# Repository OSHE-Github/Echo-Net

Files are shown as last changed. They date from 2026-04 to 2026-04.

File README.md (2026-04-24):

# Echo-Net

This project aims to assist bat research by creating a small lightweight external RFID tracking device. This device would allow researchers to easily tag bats with external tags, reducing the invasiveness of the process and allowing them to obtain data on the movement of bats. 

While these devices are being developed with the intention of bats in mind their applications can stretch beyond that of bats. This project sets a platform for using small RFID tags to track not just animals but anything that can be tagged, allowing for branching in fields such as inventory management or item tracking.

<div align="center">
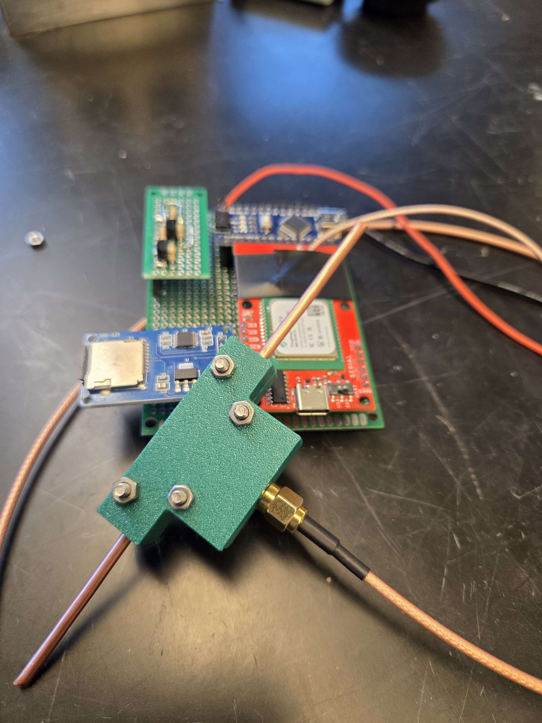
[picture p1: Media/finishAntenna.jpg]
Final Assembled Reader


Figure 1: Final Reader Prototype
</div>

# Problem Statement
In the UP bats are being killed due to an invasive fungus called the white noise fungus. This is causing a sharp decline in the bat population. A group of researchers at the Michigan Technological University CFRES Department are working to research these bats and attempt to counteract the effects of this fungus. One of their goals is to track the movement of the bats during the winter months, evaluating how they travel between hibernaculums. 

Their current strategy for tracking the bats is color tags which are attached to the wing of the bat and then manually counted through the winter to get a rough estimate of their movement patterns. The goal of this project is to design a system that utilizes small RFID tags to track the bats remotely through a system at the entrance of the cave to determine when and where the bats are moving. In addition a handheld device will also be designed for the cave to be swabbed for the current bat that are present.

# Methodology
## Overview 

To start the design a general block diagram of the system was laid out as seen in Figure 2. This system has three main sections, one of which was manually focused on this semester in the data. The power system was also evaluated, and the interrupt system was left for future semesters.

<div align="center">
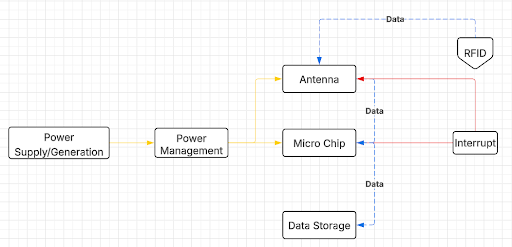
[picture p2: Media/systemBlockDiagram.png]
System Block Diagram for Reader


Figure 2: System Block Diagram for Reader
</div>

## Power

Solar energy was evaluated early in the design process but rejected due to the persistent snow cover that would obscure panels for weeks or months, and the maintenance challenges, as clearing snow is not feasible for this remote operation.

Given these constraints, wind energy was the only viable renewable power source capable of providing continuous, unattended operation throughout the winter season.

The turbine was developed for deployment near cave environments where bat activity is dense and unpredictable. Because of this, the mechanical subsystem had to meet strict biological safety requirements. The project guidelines emphasized that no component of the power-generation system could pose a serious risk of injury to the bats.

Traditional horizontal‑axis turbines with exposed, high‑speed blades were immediately ruled out due to their high tip‑speed ratios that could harm the bats.

To satisfy the safety requirement while still enabling continuous power generation, we selected a helical‑bladed VAWT. This geometry offers several advantages in a cave‑adjacent or wildlife‑dense environment. First, there is no high‑speed blade tips because the rotational velocity is distributed more evenly along the height of the rotor. Also, there is a smooth, continuous surfaces that reduce the likelihood of injury upon incidental contact. Additionally, it has omnidirectional operation, eliminating the need for yaw mechanisms or exposed linkages. Another benefit is its lower startup torque compared to some HAWT designs, which is beneficial in low‑wind cave entrances. The helical profile also ensures more uniform torque production over the rotation cycle, reducing vibration and mechanical stress on the generator shaft.

The entire embedded system requires a small but continuous power budget. Based on preliminary load analysis of the RFID reader, microcontroller, and data‑logging components, the turbine was designed to produce 0.5–1 W under typical winter wind conditions.

To meet the 0.5–1 W requirement, the a NEMA 23 stepper motor was chosen for the design, which demonstrated an approximate 12 V peak‑to‑peak open‑circuit voltage when spun manually at expected speeds.

## Data

The first part of the data system is the reader design, this encompasses the microcontroller and module board for reading the data from the tags as well as storing it on our SD card for later data analysis.
	
For our reader module we utilized the SparkFun Simultaneous RFID Reader M7E Hecto board, this board is able to read UHF RFID such as the ones that we are using. By utilizing this development board we were able to reduce the complexity of our RFID reader ensuring increasing the speed in which we could develop a working prototype and test the other components of our system.

For the microcontroller of our project we used an Arduino Nano. We chose to use this to do the simplest of implementing, there was discussion about using an Atmega328-PU for reduced power consumption but due to the ease of implementations of the Nano we ultimately went with it. In the future if power consumption becomes a problem the design may be changed to utilize something other than an Arduino to reduce power.

The rest of the reader design consisted of a logic level shifter and a SD card module. The level shifter allows for the 5V logic of the Arduino to be shifted to the 3.3V of the SparkFun M7E Hecto board. The SD card was used to store the data that was collected by the device for later data manipulation. A full schematic over our design can be seen in Figure 3.

<div align="center">
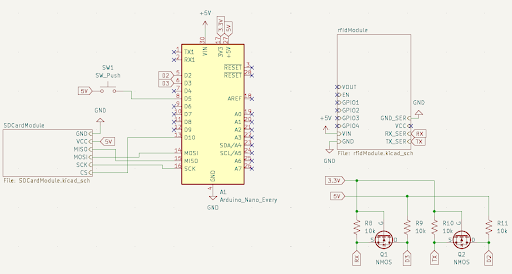
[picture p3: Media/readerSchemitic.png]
Reader Schemitic


Figure 3: Reader Schematic
</div>

The code for the reader is relatively simple. It leverages the example code from the SparkFun_UHF_RFID_Reader library constant reading example. With the addition of writing to the SD card through some simple helper functions the data collected on the SD card can be seen in Figure 4. There is also an option to enable a required trigger hold in order to start reading.

<div align="center">
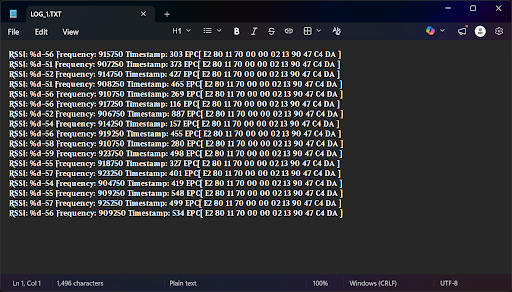
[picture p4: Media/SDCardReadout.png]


Figure 4: SD Card Data Collection Readout
</div>

The next stage in our data collected system is the antenna that is used to transmit to the tags. Three designs for an antenna were initially tested, a helical antenna, a clover leaf antenna, and a half dipole antenna. 

A ½ wave dipole antenna was decided on and constructed using copper pipe and a 3D-printed body. This resulted in an antenna that was durable, simple to construct, and lightweight/mobile. The dipole antenna was only decided on after both attempting to create other styles of antennas such as a helical and cloverleaf antenna, and after testing some 915MHz antennas we had lying around. 

The helical antenna was not selected due to its large size and directionality. It was difficult to get it aligned properly which resulted in missed reading. In addition its large size made it impractical for a hand held antenna. The cloverleaf's setbacks were in the form of its fragility and lower read range. With there being little structure to the cloverleaf, concerns around its ability to survive a winter in the cave resulted in the decision to favor the more robust half dipole design.

The initial design of this antenna was done in Matlab antenna designer, with a rendering of the half dipole antenna being seen in Figure 5. In addition the directivity of the antenna can be seen in Figure 5. This shows that the antenna can read the tags in any direction as it is circularly polarized.  Finally an S11 plot is in Figure 6, this plot as a dip at 915 MHz down to -15dB which shows that the antenna is most efficient at a frequency of 915 MHz which is desired.

<div align="center">
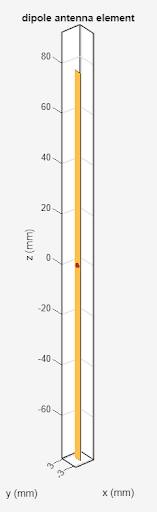
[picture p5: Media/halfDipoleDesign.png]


Figure 5: Half Dipole Antenna Design
</div>

<div align="center">
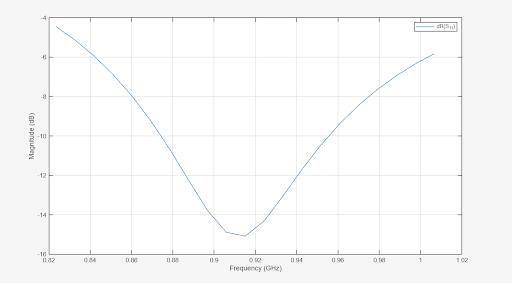
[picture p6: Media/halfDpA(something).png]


Figure 6: HalfDipole Antenna S11 Plot
</div>

The final part of our design was the selection of a tag which is attached to the bat. The tag was the Impinj Monza R6P, which can be read between the frequencies of 860 - 940 Mhz. It also has a small size of 2.6x2.6x0.8mm which help to reduce the weight that is attached to the bat.

<div align="center">
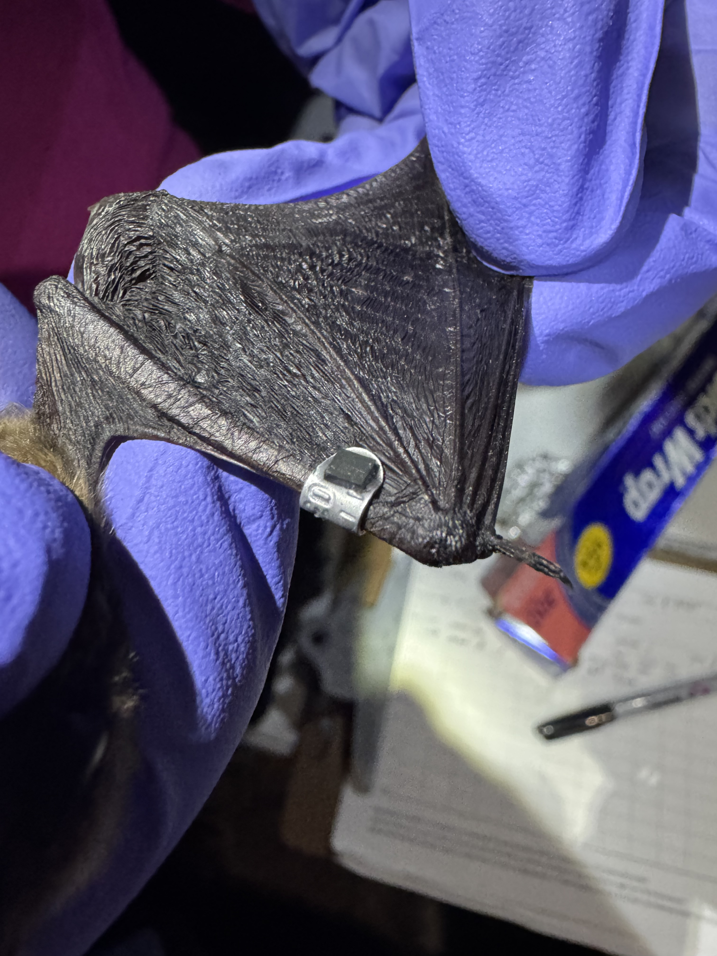
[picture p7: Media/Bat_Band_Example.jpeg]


Figure 7: Example of a Tag and Band Attached to a Bat
</div>

In addition to the tags internal antenna which is very small a circular antenna was attached to the tag as seen in Figure 8. This was done to increase the read range and directionality of the tag. By utilizing this the read range was able to be significantly increased along with making the tag easier to read in different orientations.

<div align="center">
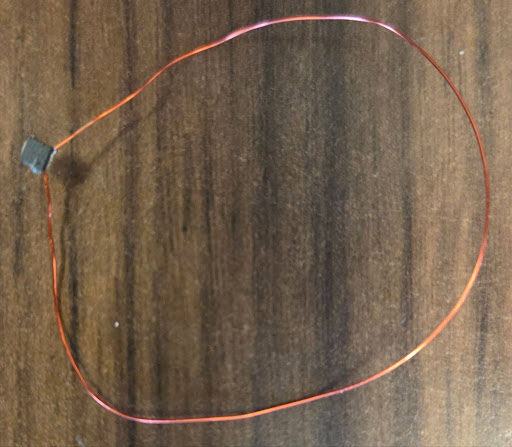
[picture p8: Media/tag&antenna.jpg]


Figure 8: Tag with Circular Antenna
</div>

# Results
## Power
The current motor in our turbine design can produce around 12V when spun in ideal condition as seen in Figure 9.  

<div align="center">
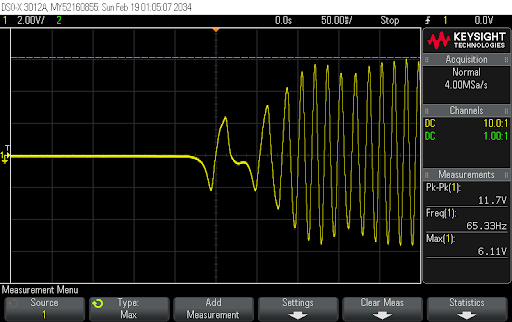
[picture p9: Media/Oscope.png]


Figure 9: Oscilloscope Readings 
</div>

To determine the amount of power that needed to be generated the power consumption of the read was measured at different dB output. The results of the this testing can be seen in Figure 10. The general operating range of this device is between  20-27 dB which means that on average  it will be consuming between 2-2.85 watts. This means that having the power completed provided my the turbine is impractical. To compensate for this battery options were evaluated.

<div align="center">
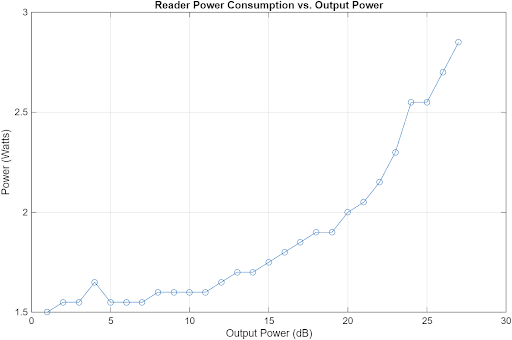
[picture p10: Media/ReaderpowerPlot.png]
Reader Schemitic


Figure 10: Read Power Consumption based on Output dB
</div>

The first battery option evaluated was a car battery that would be left at the stationary site to supplement the turbine. Assuming a car battery of 12.8V and 60 Ahr it can be determined that there 786 Whr. Assuming that there is 90% efficiency in the step down to operating voltage and that the battery should not be operated below 50%, as recommended for lead acid batterying the device could be powered for 3.83 days straight. 

Another option that was evaluated was a hand held power brick used for charging phones. An example that was found commercially available had an estimated 20,000 mAhr at 3.7V which equates to 74 Whr. Assuming the same 90% efficiency that was had with the car battery it was determined that the device could be powered for 17.8 hrs. This provides a viable hand held power solution in a light weight portable package

## Data

Using a Micro VNA the characteristics of out half dipole antenna were measured as seen in Figure 11, and summarized in Table x. This data is closely aligned with the that of the simulation with the desired S11 LOGMAG being around -15 dB and the impedance of the antenna being 50 Ω. 

<div align="center">
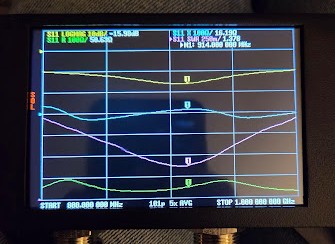
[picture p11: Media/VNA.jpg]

	
Figure 11. Nano VNA Data for Half Pole Antenna

Table 1. Data from Nano VNA for Half Pole Antenna 
| Parameter        | Setting | Value    |
|------------------|--------|----------|
| S11 LOGMAG       | 10 dB  | -15.98 dB |
| S11 R            | 100 Ω  | 50.63 Ω  |
| S11 X            | 100 Ω  | 16.19 Ω  |
| SWR              | 250 m  | 1.378    |
</div>

With this antenna design the read range was measured with 4 different configurations as seen in Figure 12. The first one was with the tag on the mental band. With this configuration no read range was able to occur. This was hypothesized to be due to the JB weld that was used to connect the tag to the band. This is further supported by the fact that when the tag is removed from the band but left in close proximity to the band the tag can be read. This leads to the belief that it is not the metal of the band that is hindering the read range. 

The next configuration that was tested was the tag with no band or additional antenna. The read range in this configuration was very limited, only around a few centimeters and was very orientation dependent. 
To compensate for the short read range a loop antenna was added to the tag to increase the range. This had an immediate effect with the read range jumping up to 1-1.5 meters and the tags being less orientation dependent while being read. In addition while not being consistent that the maximum range the tags were detected up to was 2.5m. 
<div align="center">
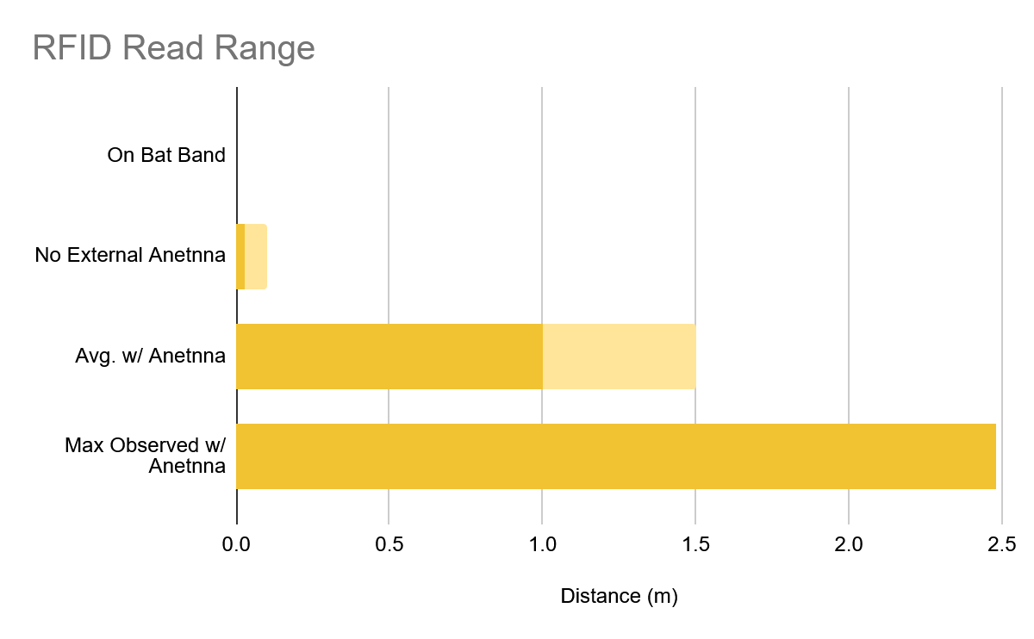
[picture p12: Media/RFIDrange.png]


Figure 12. Read Range of the Tags in Different Configurations
</div>

# Future Work
To advance this project forward custom flex PCBs will be designed such as the reference in Figure 13. This flex PCB will then be epoxied to the banners with the additional loop antenna confined with them. To determine the optimal antenna design multiple lengths, widths, and dielectrics will be tested. By creating a swab of these antenna designs it will be able to determine the ideal design for read range. 
<div align="center">
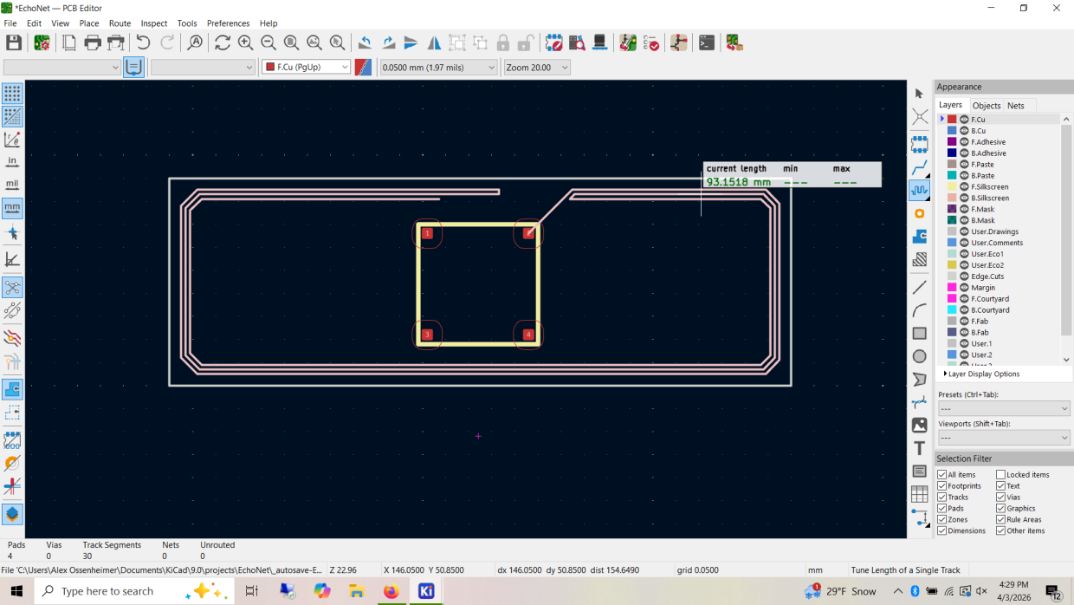
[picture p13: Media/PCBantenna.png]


Figure 13. Mock-Up of Possible PCB Antenna 
</div>

In addition to this a PCB will also be designed for the reader design. Currently it is only a prototype board which works great for testing and rapid prototyping but for future designs a PCB will be made to make it more robust and easier to assemble. 
Additional testing also needs to be completed for battery option testing. Two options were evaluated for viability but neither has yet been tested to confirm life span. In addition the trickle charge from the wind turbine should be added into the life span of the car battery option. In addition to this to decrease power consumption low power interpret monitoring can also be evaluated.

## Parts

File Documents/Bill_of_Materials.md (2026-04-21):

# Bill of Materials (BOM)

## Wind Turbine

| Part | Quantity | Price |
|------|----------|-------|
| [23HS45-4204S Nema 23 Motor](https://www.omc-stepperonline.com/nema-23-bipolar-3nm-425oz-in-8mm-diameter-4-2a-57x57x113mm-4-wires-stepper-motor-23hs45-4204s1) | 1 | $28.70 |
| [3' 6061 Solid Aluminum Rod 10mm Diameter](https://www.mcmaster.com/products/aluminum-rods/material~aluminum-2/material~6061-aluminum/) | 1 | $8.73 |
| [⅛" Aluminum TIG Welding Rods](https://www.airgas.com/product/Welding-Products/Filler-Metal/TIG-Rod-%28GTAW%29/TIG-Rod---Aluminum/p/RAD64001731) | 1 Tube | $19.81 |
| [10 mm Flanged Bearings](https://www.amazon.ca/uxcell-F6900ZZ-10x22x6mm-Shielded-Bearings/dp/B07Z3DQHLL) | 2 pcs (1 set) | $6.89 |
| [JB Weld KwikWeld](https://www.amazon.com/Epoxy-Adhesives-J-B-Weld/s?keywords=Epoxy+Adhesives&rh=n%3A256244011%2Cp_89%3AJ-B%2BWeld&c=ts&ts_id=256244011) | 1 pack | $5.93 |

## Dipole Antenna

| Part | Quantity | Price |
|------|----------|-------|
| [8 Gauge Wire](https://www.amazon.com/Tynulox-Refrigeration-Seamless-Jewellery-Industry/dp/B0BLNRQYZ4/ref=sr_1_4_sspa?s=industrial) | 2 x 73cm | $7.39 |
| [Male SMA Port](https://www.amazon.com/wlaniot-Connector-Coaxial-Bulkhead-Terminal/dp/B078H4F8R6/ref=sr_1_6) | 1 | $7.99 |
| [22 Gauge Wire](https://www.amazon.com/TUOFENG-Hookup-Wires-6-Different-Colored/dp/B07TX6BX47/ref=sr_1_8?s=industrial) | ~50cm | $15.89 |
| [PETG](https://www.prusa3d.com/product/prusament-petg-jungle-green-1kg-nfc/) | ~9.4g | $0.26 |

## Reader Module

| Part | Quantity | Price |
|------|----------|-------|
| [SparkFun Simultaneous RFID Reader M7E Hecto](https://www.sparkfun.com/sparkfun-simultaneous-rfid-reader-m7e-hecto.html) | 1 | $309.95 |
| [Arduino Nano](https://www.amazon.com/LUIRSAY-2Pcs-ATmega328P-Microcontroller-Compatible/dp/B0F1FQMNXM/ref=sr_1_1?hvqmt=e&mcid=8b35fce829b232af874780ddece88d5b) | 1 | $12.99 |
| [Prototyping Board](https://www.amazon.com/ELEGOO-Prototype-Soldering-Compatible-Arduino/dp/B072Z7Y19F/ref=sr_1_1_sspa) | 1 pack | $8.99 |
| [2.54mm Male/Female Headers](https://www.amazon.com/2-54mm-Breakaway-Female-Connector-Arduino/dp/B01MQ48T2V/ref=sr_1_6?s=industrial) | 1 pack | $7.99 |
| [10kΩ THM Resistor](https://www.digikey.com/en/products/detail/stackpole-electronics-inc/CF14JT10K0/1741265) | 4 | $0.10 |
| [VN2106N3-G BJT](https://www.digikey.com/en/products/detail/microchip-technology/VN2106N3-G/4902398) | 2 | $0.50 |
| [UFL to SMA Adapter](https://www.amazon.com/Ahoaepy-Coaxial-Pigtail-Extension-Antenna/dp/B0D29JTYPK/ref=sr_1_2_sspa?hvlocint=4089&hvqmt=e&mcid=b62bc0d9b4873ecfa4f331e8886e656e) | 1 | $7.19 |
| [SMA Male to Male Jumper](https://www.amazon.com/coaxial-Antenna-Extender-Adapter-Jumper/dp/B092Z88R2T/ref=pd_sbs_d_sccl_2_11/138-8639619-0532315) | 1 | $8.99 |
| [SD Card Module](https://www.amazon.com/Integrated-Circuit-Interface-Raspberry-Breakout/dp/B08C4WY2WR/ref=sr_1_5?hvqmt=e&mcid=e3acc2ea9a2638039ac6f78958a5b55b&s=electronics) | 1 | $5.99 |

## Total Cost: $504.07

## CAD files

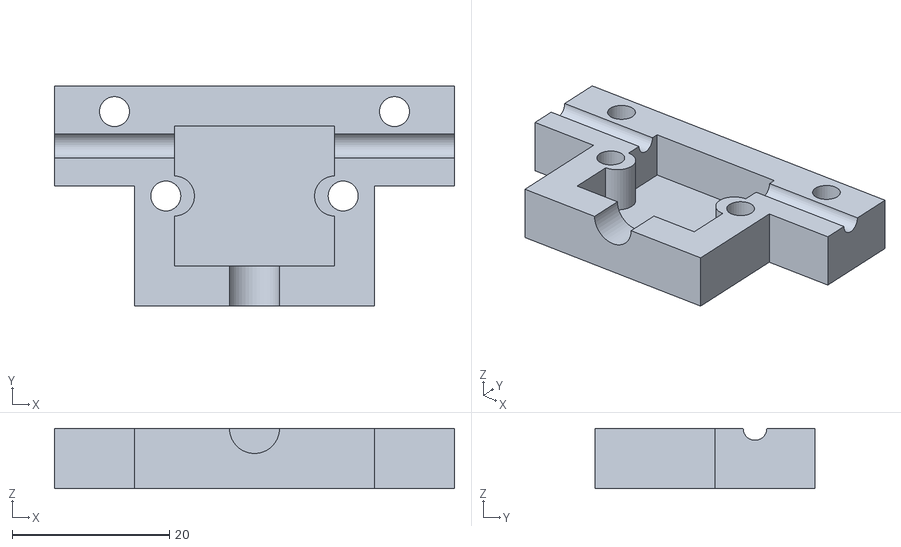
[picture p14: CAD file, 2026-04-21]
CAD/Antenna/Dipole_Antenna_Shell.stl
50.8 x 27.9 x 7.62

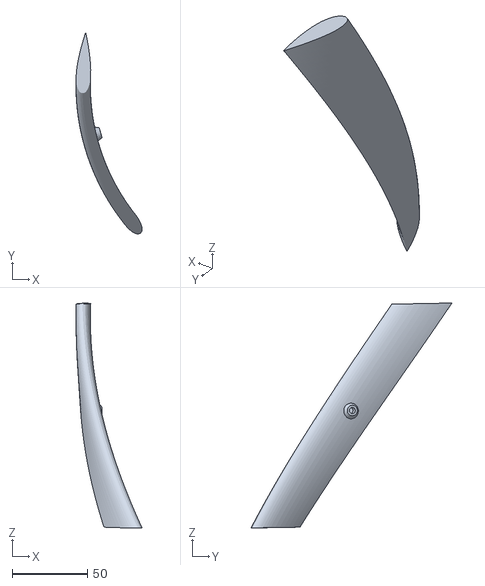
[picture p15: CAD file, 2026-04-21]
CAD/Turbine/VAWT_Fin_Top.stl
43.8 x 133.3 x 149.2

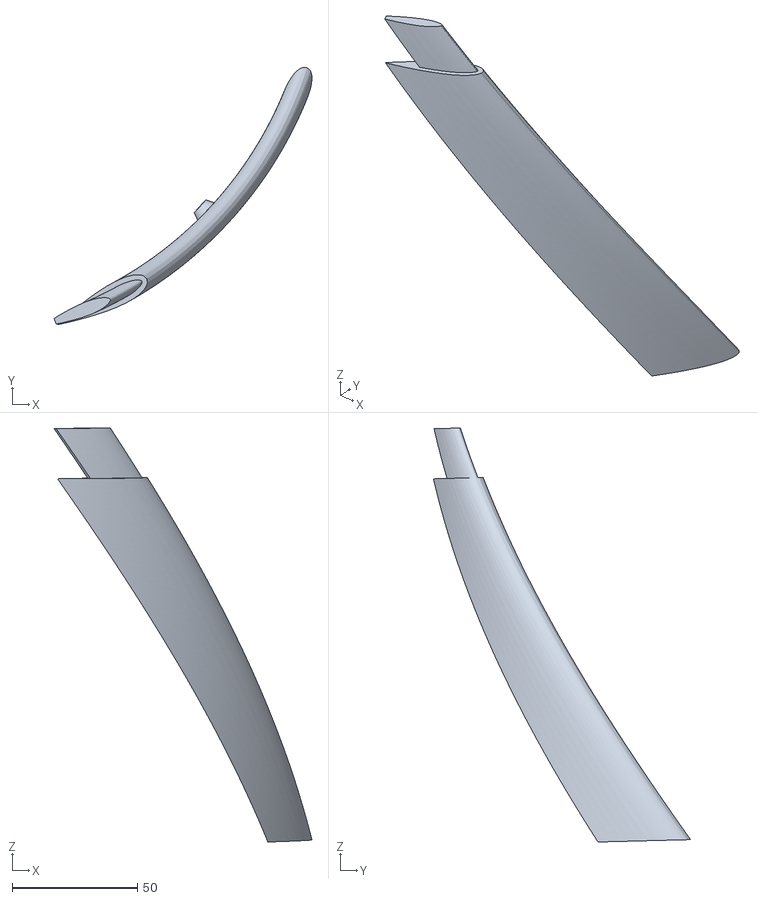
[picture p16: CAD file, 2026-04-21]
CAD/Turbine/VAWT_Fin_Bottom.stl
103.0 x 102.7 x 165.3

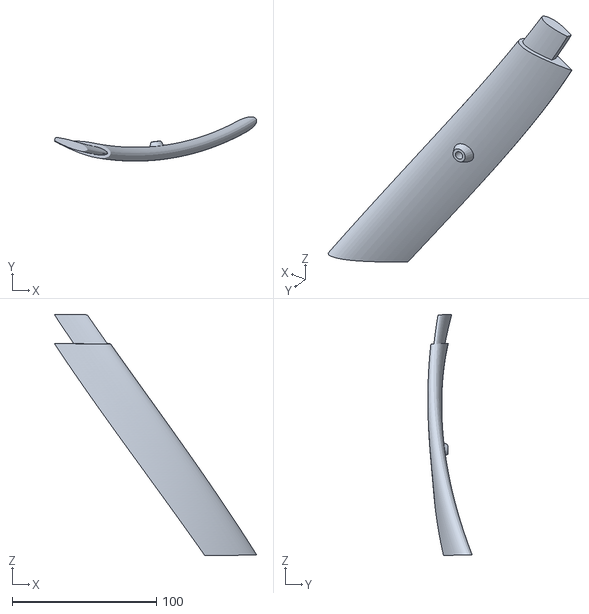
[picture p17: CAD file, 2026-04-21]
CAD/Turbine/VAWT_Fin_Middle.stl
140.1 x 30.7 x 166.9

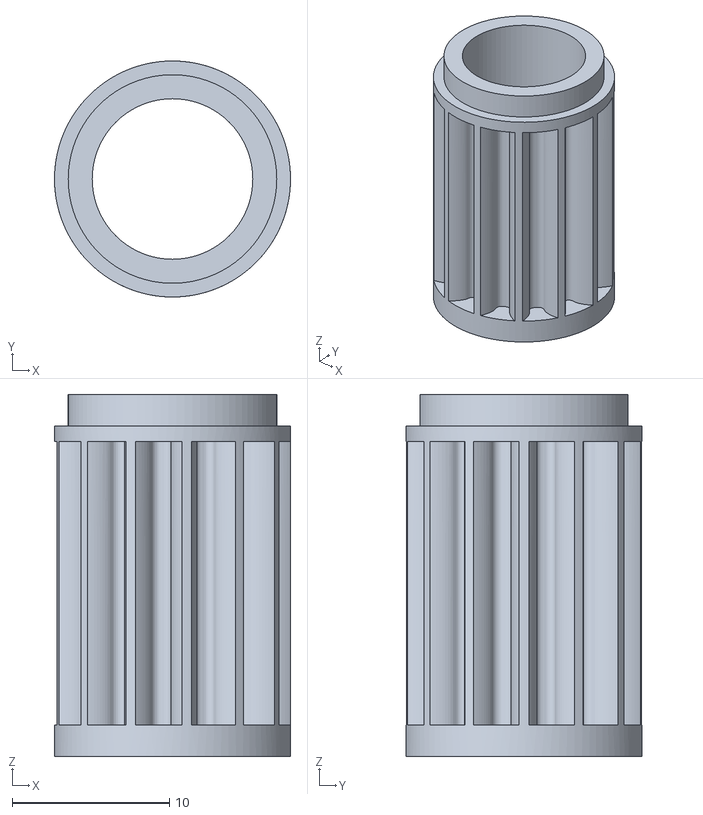
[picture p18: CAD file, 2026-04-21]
CAD/Turbine/Spur Gear 13 teeth.stl
15.0 x 15.0 x 23.0

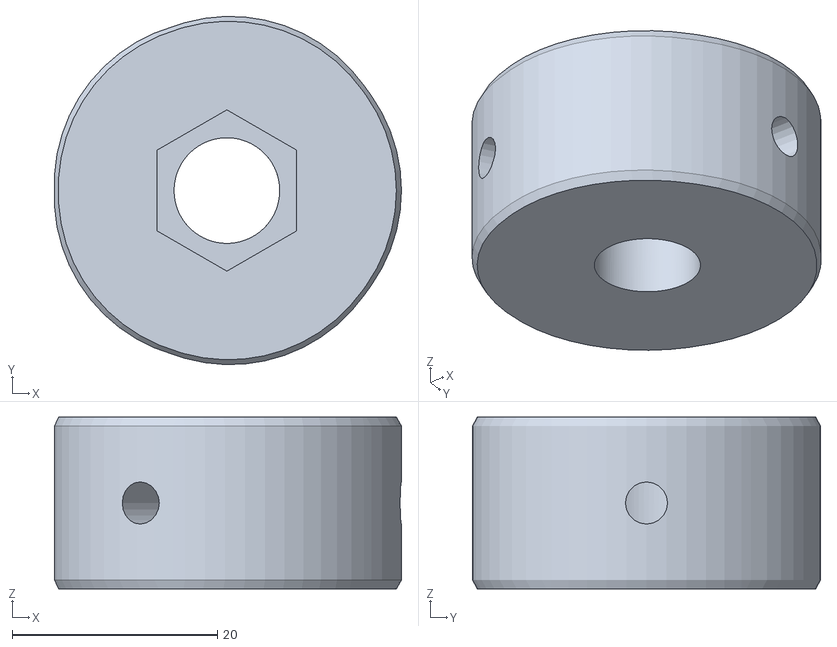
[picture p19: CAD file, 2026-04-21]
CAD/Turbine/PoleConnector.stl
33.8 x 33.9 x 16.7

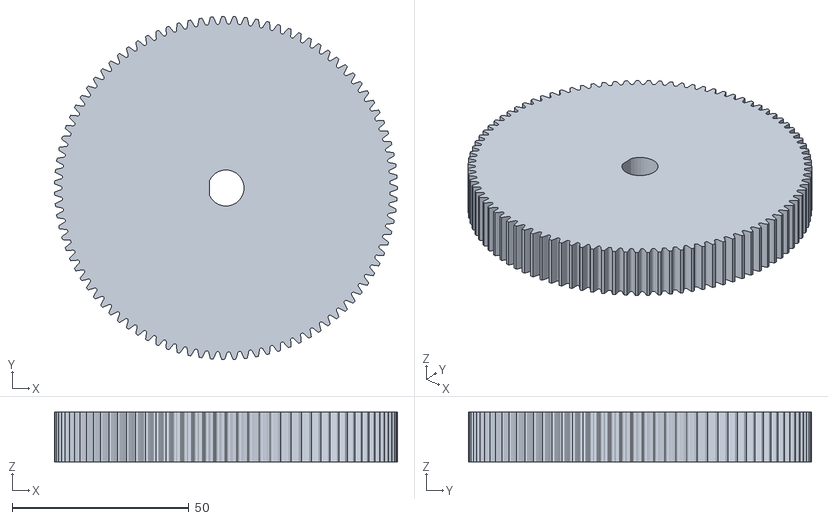
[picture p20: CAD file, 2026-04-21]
CAD/Turbine/Spur Gear 95 teeth.stl
97.0 x 97.0 x 14.0

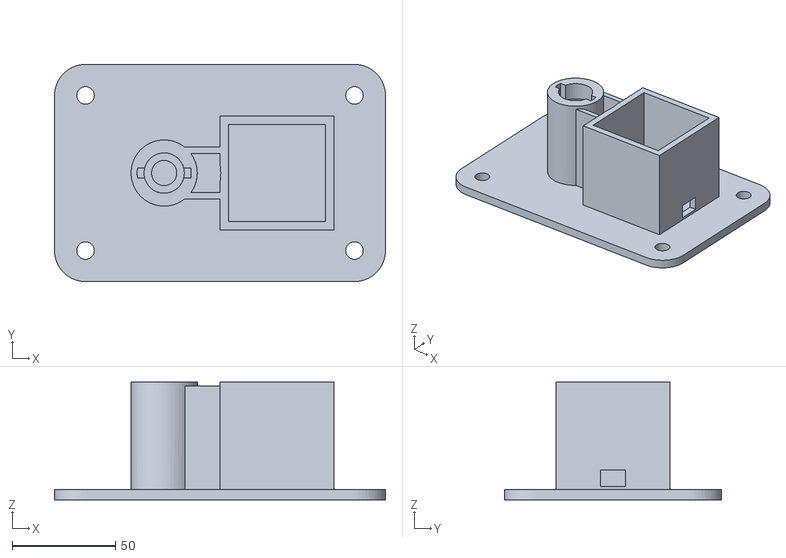
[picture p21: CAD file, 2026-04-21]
CAD/Turbine/MotorAndShaftCase.stl
160.0 x 105.0 x 57.0

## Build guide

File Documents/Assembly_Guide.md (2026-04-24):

# Turbine    
Outlined Instruction Steps:

1. Print 3D printed parts  
   1. 3 “Top” pieces  
   2. 3 “Bottom” pieces  
   3. 9 “Middle” pieces  
   4. 5 Spoke shaft collars  
   5. 1 Motor Gear  
   6. 1 Shaft Gear  
   7. [Link to files](../CAD/Turbine)  
2. Cut spokes to 15 cm (15 total spokes)
<div align="center">
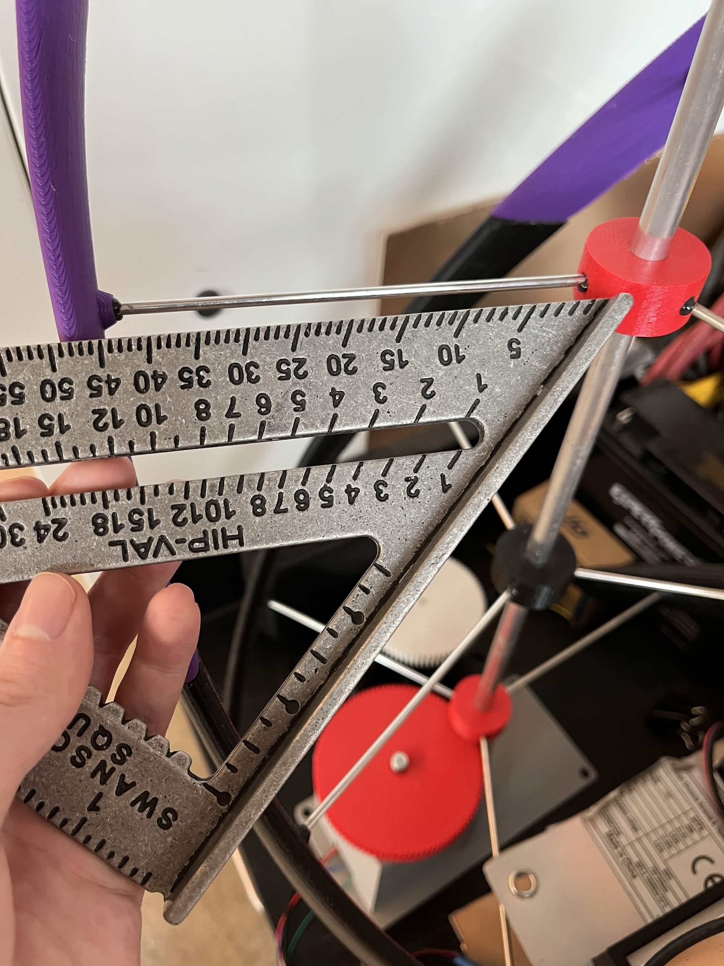
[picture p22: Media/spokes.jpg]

</div>

3. Place motor and bearings in place in the motor housing
<div align="center">
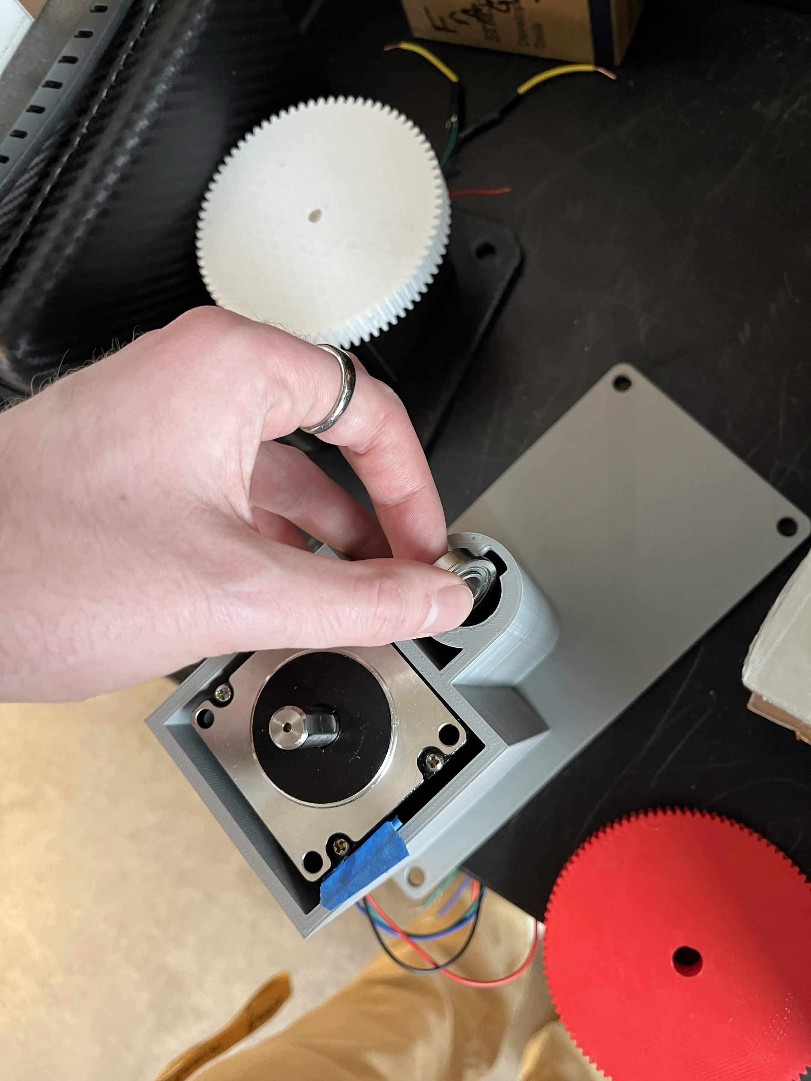
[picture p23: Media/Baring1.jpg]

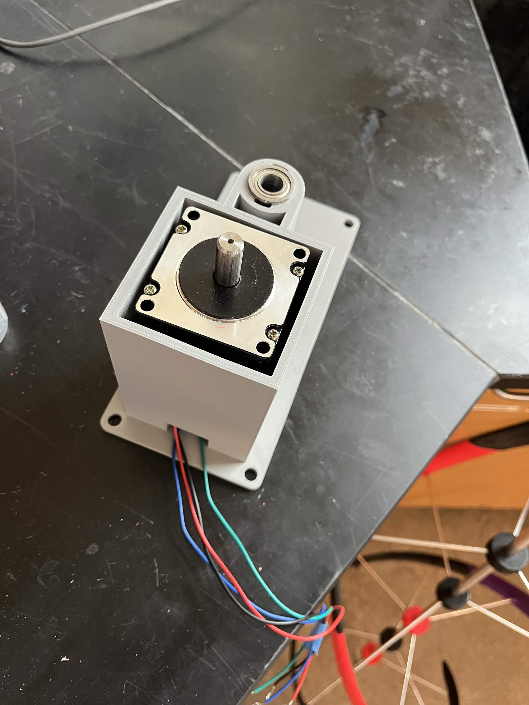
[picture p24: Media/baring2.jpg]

</div>

4. Put the motor gear on motor shaft
<div align="center">
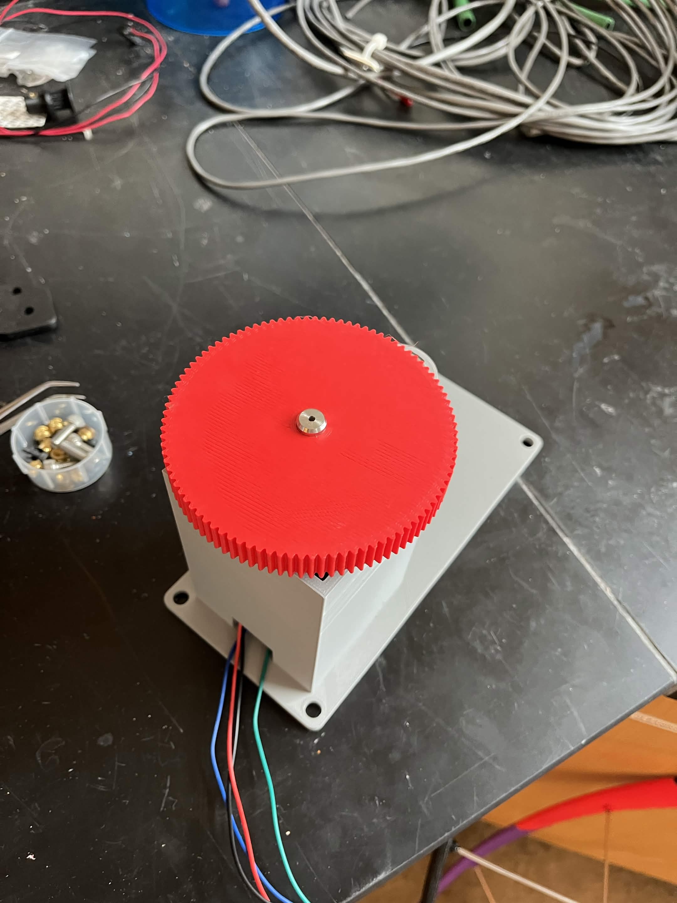
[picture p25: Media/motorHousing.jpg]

</div>

5. Epoxy / JB Weld spokes into shaft collars
<div align="center">
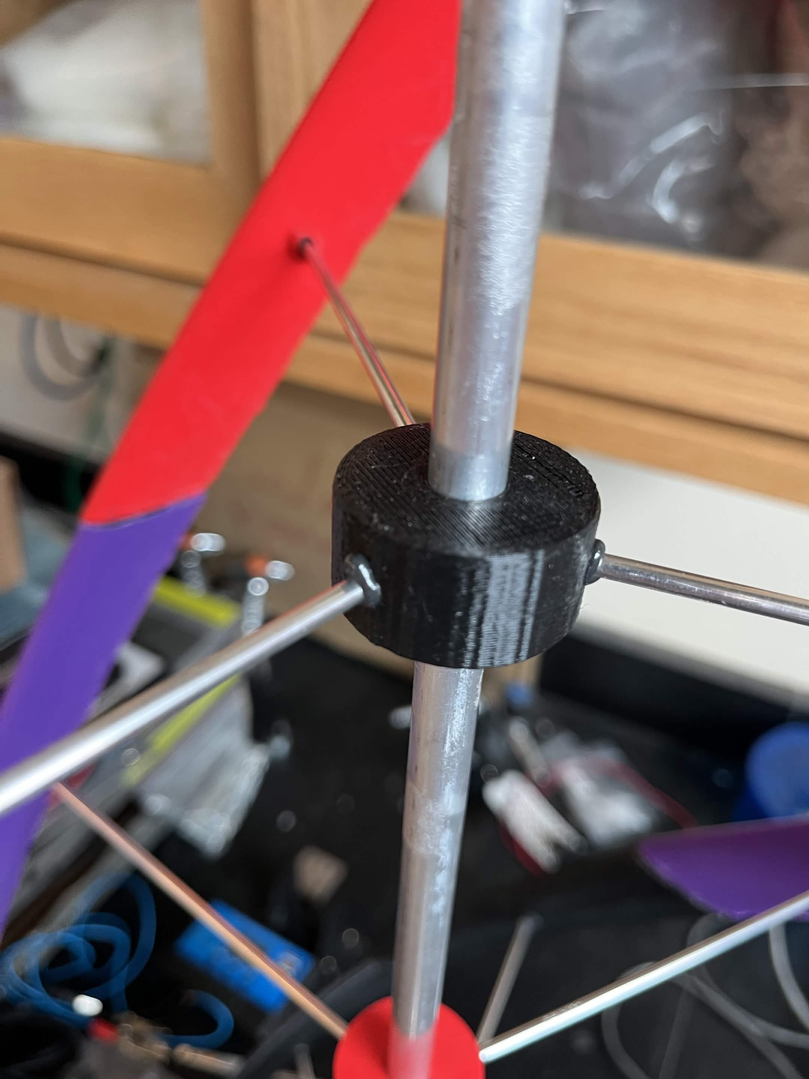
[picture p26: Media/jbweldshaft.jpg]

</div> 

6. Attach shaft collar items on the shaft (shaft gear, blade attachment points) either by friction or with an adhesive (if using adhesive, wait until the blades are connected to the spokes for proper spacing)
<div align="center">
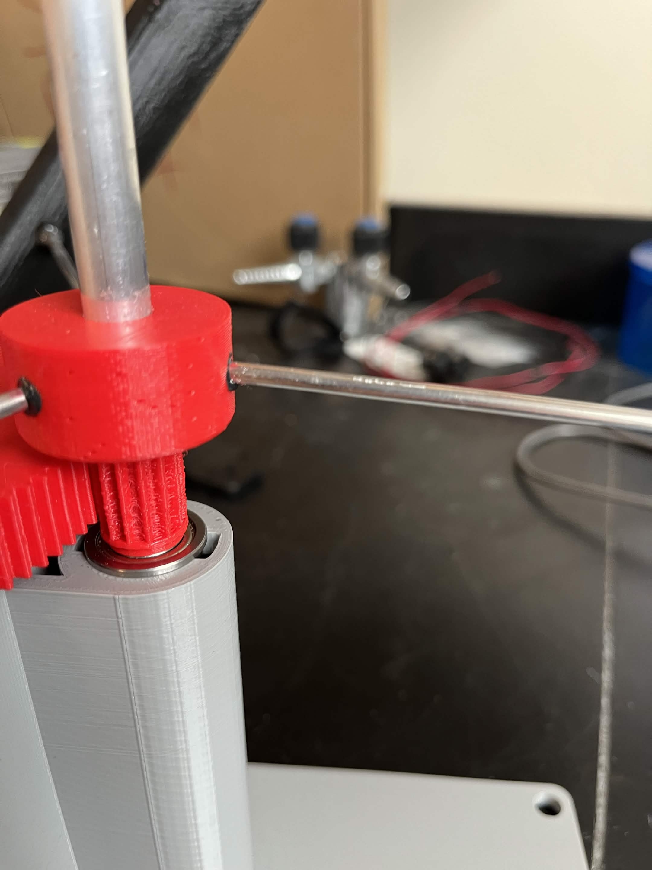
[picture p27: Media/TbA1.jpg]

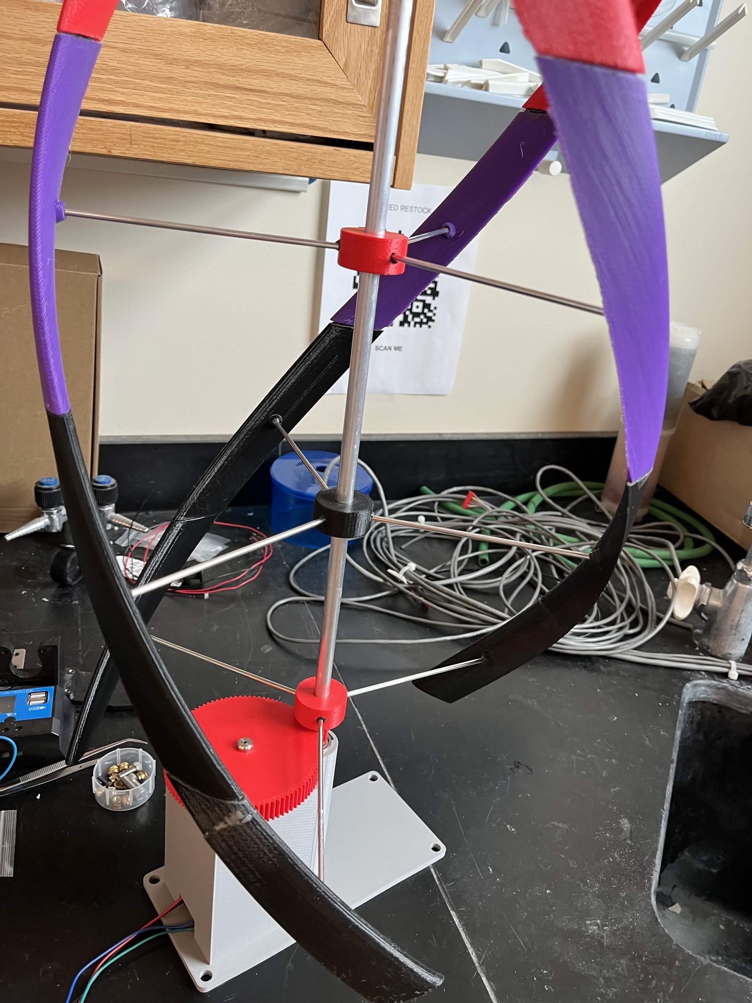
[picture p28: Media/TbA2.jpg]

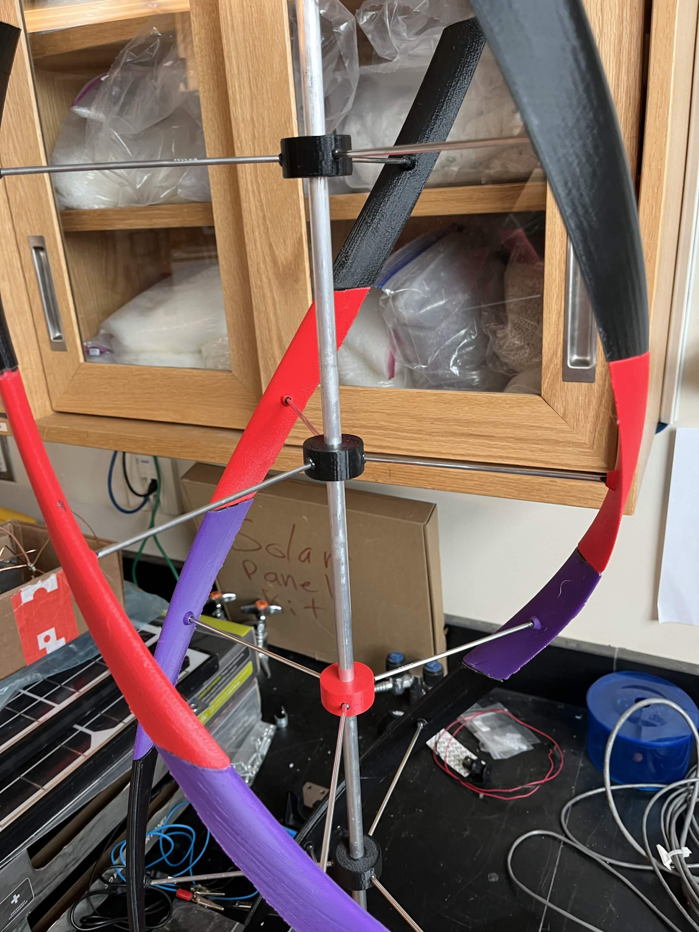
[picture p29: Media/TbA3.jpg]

</div>

7. Epoxy / JB Weld spokes into blades while the spokes and shaft collar attachment points are on the turbine (and epoxy the blades together)
<div align="center">
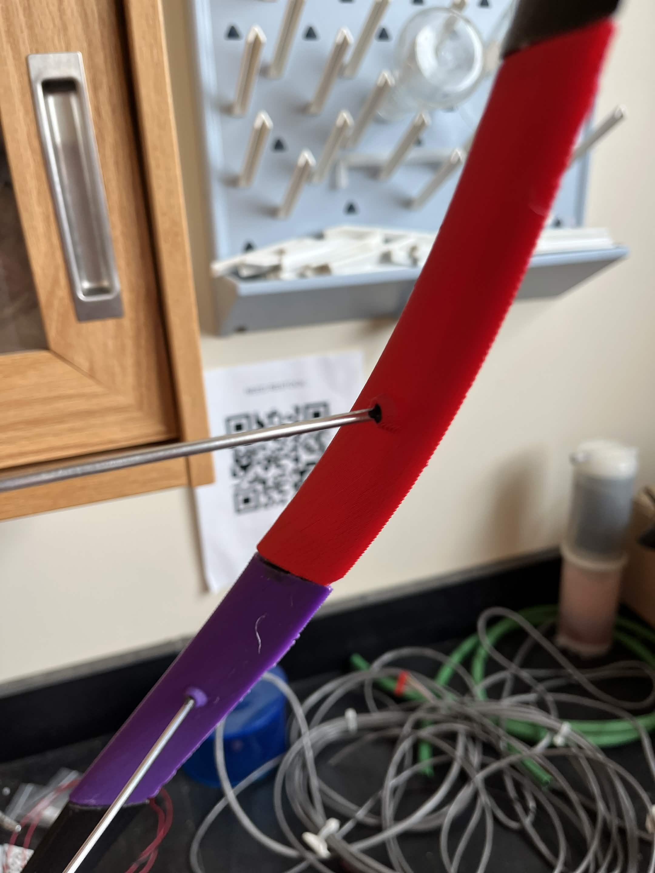
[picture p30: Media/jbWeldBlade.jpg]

</div>

8. Once assembled the final product should look like the turbine seen below
<div align="center">
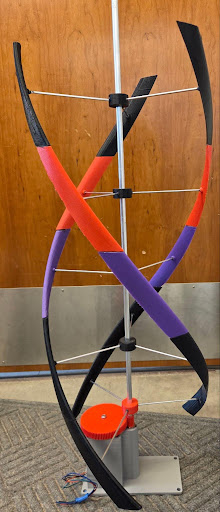
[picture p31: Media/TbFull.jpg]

</div>

# Reader

1. Solder female headers onto a large piece of prototyping board in a manner that will alow the SparkFun M7E Hector, the Arduino, and the SD card reader to be mounted (making sure to leave room for a level shifter)  
2. Solder together the level shifter on a separate piece of prototyping board with a male header  
3. Add the appropriate female header to the main proto board  
4. Solder together all the 5V rails, 3.3V rails, and GND rails using wires and solder bridges on the bottom side of the main board  
5. Solder the Arduino's TX and RX pins to the low side of the level shifter  
6. Solder the SparkFun M7E Hecto’s TX and RX pins to the high side of the level shifter (making sure that through the level shifter, the RX pin of the Arduino board connects to the TX pin on the SparkFun board and vice versa)  
7. Follow the wiring diagram to solder the signal lines to the SD card reader and Arduino (→MISO, →MOSI, →SCK, →CS)  
<div align="center">
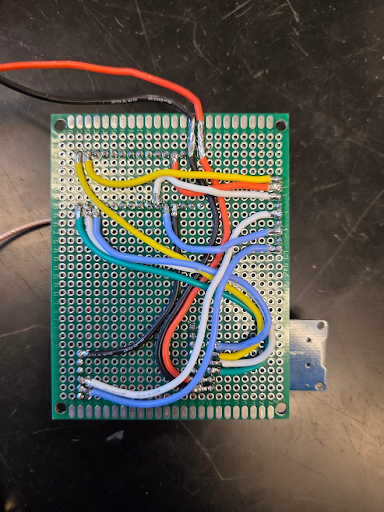
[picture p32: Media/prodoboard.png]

</div>  

8. Compile and upload the code to the Arduino using the Arduino IDE

# Antenna 

1. Download the .stl file for the antenna case   
2. 3D print the case   
   1. Requires two of the same prints sides are identical  
        
<div align="center">
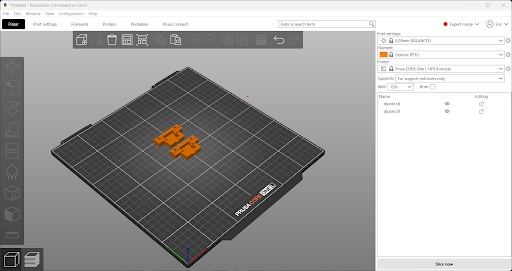
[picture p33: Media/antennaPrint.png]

</div>
        
3. Cut 2 pieces of 8 Gauge copper wire to 73 cm  
4. Use a hammer to flat one end of the wire  
5. Drill a small hole through the flatten copper   
   1. This hole helps with thermal relief when soldering   
<div align="center">
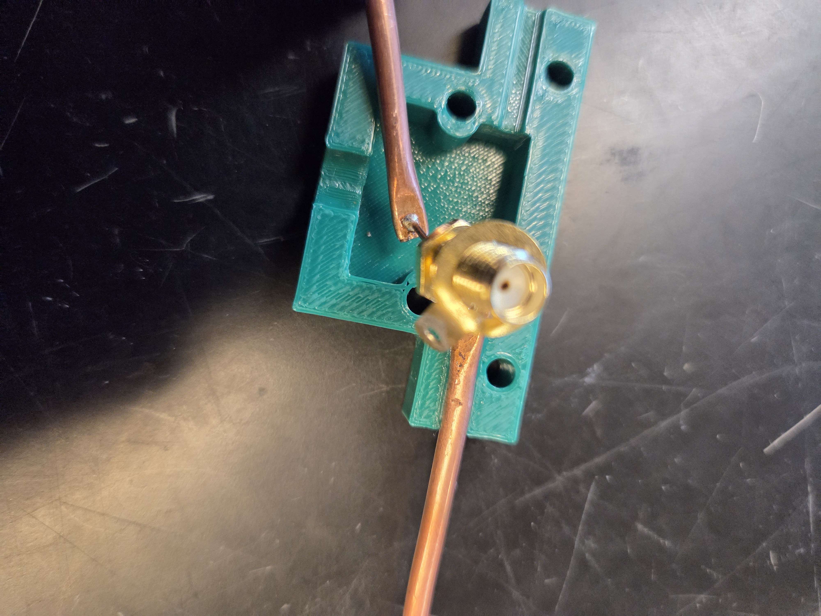
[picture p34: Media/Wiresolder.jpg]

</div> 
        
6. Solder a small wire between your SMA port and the hole in the coper wire  
   1. Make sure the wire is long enough so that the copper wire can sit in the grooves and reach the bottom where the SMA port is   
<div align="center">
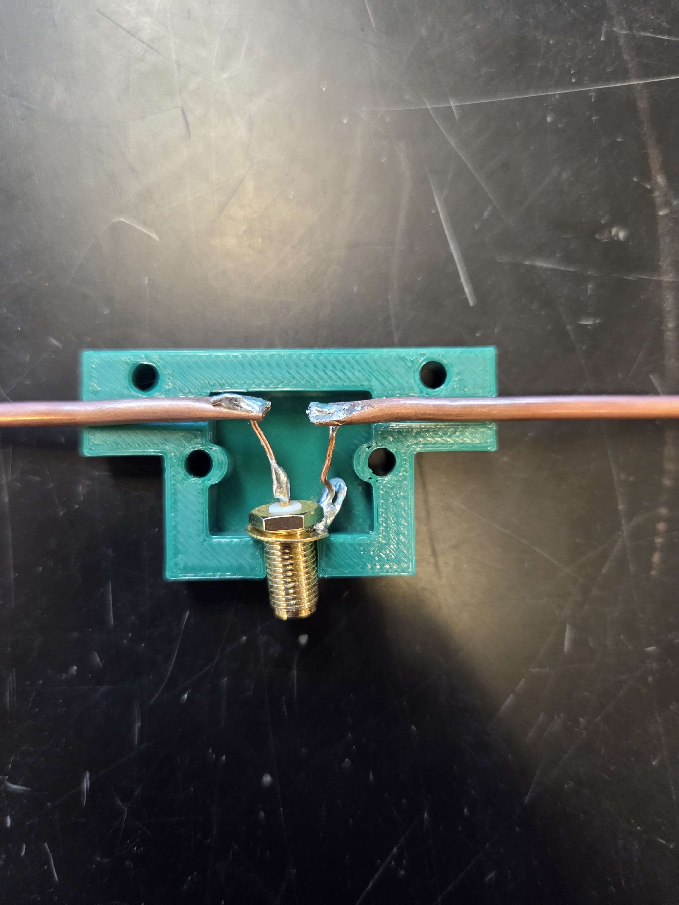
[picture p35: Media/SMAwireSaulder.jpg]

</div> 
       
7. Confirm that copper wires and SMA port are in the proper position before screwing the two sides together  
8. Connect antenna to SMA port of reader  
<div align="center">
Final Assembled Reader
</div>

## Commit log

2026-04-21 Add initial Bill of Materials file
2026-04-21 Add Assembly Guide document
2026-04-21 Create Bill of Materials with components and costs
    Added detailed sections for Wind Turbine, Dipole Antenna, and Reader Module with parts, quantities, and prices.
2026-04-21 Rename Bill of Materials to Bill_of_Materials.md
2026-04-21 Add image of final assembled reader
    Added an image of the final assembled reader to the README.
2026-04-22 More reader stuff
    Updated the Problem Statement and Methodology sections for clarity and added details about the power and data systems used in the project.
2026-04-23 Can I sleep now?
    Added figures and descriptions for the reader prototype, system block diagram, and antenna design. Enhanced the explanation of the tag and its antenna for improved clarity.
2026-04-23 last time i didnt save it was bad
    Updated formatting and section headers in the assembly guide.
2026-04-23 turbine done??
    Updated links and added images for assembly instructions.
2026-04-23 waiting on 2 pictures yet then done mostly
    Added results and future work sections to the README, detailing power generation, battery options, antenna measurements, and planned PCB designs.
